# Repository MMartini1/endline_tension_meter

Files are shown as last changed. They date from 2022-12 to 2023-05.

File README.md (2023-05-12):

# endline_tension_meter
 Submersible load cell based endline tension meter

Original design by William DeVoe, Marine Resource Scientist at Maine Department of Marine Resources 

This version is built for the NOAA Northeast Fisheries Science Center and is a work in progress.  The main differences are:
- 3D printed framework to secure the electronics
- detachable wires from the end cap switch
- Qwiic shield to connect from the feather to the sensor board
- different load cell wiring
- larger battery and housing for 6 day endurance 
- add pressure relief valve
- refinements to the code

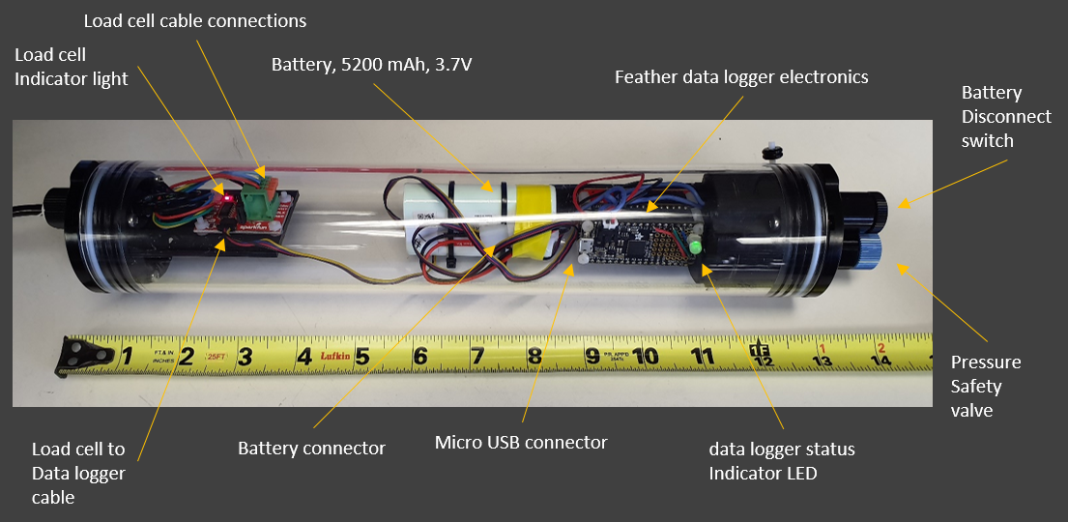
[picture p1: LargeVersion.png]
Image of the load cell logger


This repository is a scientific product and is not official communication of the National Oceanic and Atmospheric Administration, or the United States Department of Commerce. All NOAA GitHub project code is provided on an ‘as is’ basis and the user assumes responsibility for its use. Any claims against the Department of Commerce or Department of Commerce bureaus stemming from the use of this GitHub project will be governed by all applicable Federal law. Any reference to specific commercial products, processes, or services by service mark, trademark, manufacturer, or otherwise, does not constitute or imply their endorsement, recommendation or favoring by the Department of Commerce. The Department of Commerce seal and logo, or the seal and logo of a DOC bureau, shall not be used in any manner to imply endorsement of any commercial product or activity by DOC or the United States Government.

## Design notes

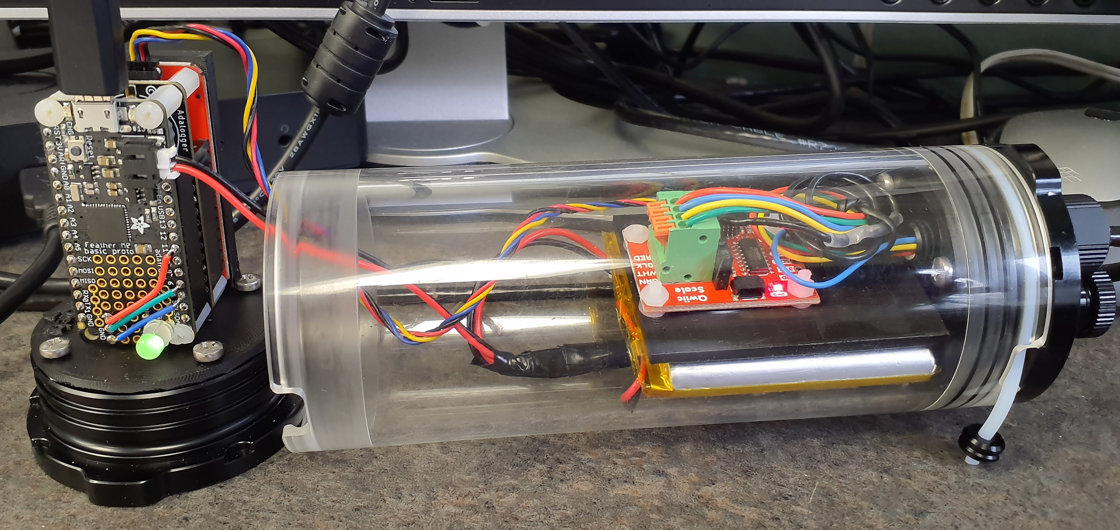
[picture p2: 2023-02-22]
Images/20230206_125726web.jpg

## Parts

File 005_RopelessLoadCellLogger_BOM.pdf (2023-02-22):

Endline Tensiometer Bill of Materials | TOTAL | $ 3,281.87
Purpose/Assembly | Vendor | Item description or part number | Qty | unit cost | total cost | stock #
Load Cell | Load Cell Central Load Cell Central UMLS-51-4.75t on shackle | 1 $ 2,795.00 $ 2,795.00
Load Cell - spare | McMaster | 316 Stainless Steel Cotter Pin
| | 1/8" Diameter, 2" Long, pack of 25 | 1 | | 18.18 $ | 18.18 98355A170
Logger | Adafruit | Adafruit Feather M0 Basic Proto | 1 | 19.95 $ | $ | 19.95 | 2772
Logger alternative | Adafruit | Adafruit Feather M0 Express - ATSAMD21 Cortex M0,
Product ID: 3403 | $ | 19.95 $ | - | 3403

possible logger alternative Adafruit

| | Adafruit Feather M4 Express - Featuring ATSAMD51 -
ATSAMD51 Cortex M4, Product ID: 3857 | $ | 22.95 $ | - | 3857
Logger | Adafruit | Adalogger FeatherWing: SD + RTC | 1 $ | | 8.95 $ | 8.95 | 2922
Logger | Digikey | NAU7802 Weight Scale Sensor Qwiic Platform
Evaluation Expansion Board, Sparkfun SEN-15242, | 1 | 16.50 $ | $ | 16.50 1568-SEN-15242-ND
Logger | Adafruit | Stacking Headers for Feather - 12-pin and 16-pin
female headers, Product ID: 2830 | 3 | 1.25 $ | $ | 3.75 | 2830
Logger | Sparkfun | SparkFun Qwiic Shield for Thing Plus | 1 $ | | 2.97 $ | 2.97 DEV-16790
| Sparkfun | Sparkfun Qwiic Cable
Logger | Western Digital Micro SD Card, 32GB | 2 $ | 10.29 $ | 20.58 SDSQXAF-032G-GN6MA
Logger | Digikey | Coin, 12.5mm Lithium Manganese Dioxide 3 V Battery
Non-Rechargeable (Primary), CR1220 | 2 | 1.13 $ | $ | 2.26 P033-ND
Logger | Adafruit | Diffused RGB 5mm LED (25 pack), Product ID: 302
(common anode) | 1 | 12.50 $ | $ | 12.50 | 302
Logger | Adafruit | Through-Hole Resistors - 22K ohm 5% 1/4W - Pack of
25, Product ID: 2785 | 1 | 0.75 $ | $ | 0.75 | 2785
Logger | Adafruit | Lithium Battery, 2500 mAh LiPo, 3.7v, Product ID 328 | 2 | 14.95 $ | $ | 29.90
Logger - Spare | Digikey | Pushbutton Switch SPST-NO Standard Panel Mount,
Rear, Grayhill P/N 30-3UL, GH1358-ND | $ | 6.26 $ | - GH1358-ND
Logger | Digikey | 0.110" (2.79mm), 0.125" (3.18mm) Quick Connect
| | Female 18-22 AWG Crimp Connector Fully Insulated,
TE Faston 2-520084-2, A27797-ND | 2 | 0.45 $ | $ | 0.90 A27797-ND
005_LoadCellLogger_BOM.xlsx | Page 1

Logger - development | Digikey | Qwiic Cable - Breadboard Jumper (4-pin), Sparkfun
PRT-14425, | 1 | 1.50 $ | $ | 1.50 1568-1709-ND
Logger | Digikey | Flexible Qwiic Cable - 200mm, Sparkfun PRT-17258
ROHS | 1 | 1.60 $ | $ | 1.60 1568-PRT-17258-ND
Logger | Adafruit | FeatherWing Proto - Prototyping Add-on For All
Feather Boards | 1 | 4.95 $ | $ | 4.95 2884
Logger | Digikey | Hex Standoff Threaded M2.5x0.45 Nylon 0.394"
(10.00mm), M2105-2545-N, 1772-2274-ND | 4 | 3.15 $ | $ | 12.60 1772-2274-ND
Logger | Digikey | Hex Standoff Threaded M2.5x0.45 Nylon 0.394"
(10.00mm), RAF M1257-2545-N, 1772-2050-ND | 4 | 1.73 $ | $ | 6.92 1772-2050-ND
Logger | Digikey | M2.5x0.45 Pan Head Machine Screw Phillips Drive
| | Nylon, Essentra 50M025045P012, 145-
50M025045P012-ND | 8 | 0.15 $ | $ | 1.20 145-50M025045P012-ND
Logger | Digikey | M2.5x0.45 Hex Nut 0.190" (4.83mm) Nylon, Essentra
04M025045HN, RPC7085-ND | 8 | 0.12 $ | $ | 0.96 RPC7085-ND
Logger | Digikey | USB 2.0 Cable A Male to Micro B Male 3.28' (1.00m)
Shielded, CNC 102-1492-BL-F0100, 1175-1809-ND | 2 | 6.16 $ | $ | 12.32 1175-1809-ND
Logger | Adafruit | battery charger | 1 $ | 6.95 $ | 6.95 | 1904
Logger | Adafruit | JST PH 2-Pin Cable - Female Connector 100mm
Product ID: 261 | 1 | 0.75 $ | $ | 0.75 | 261
Logger | Adafruit | JST PH 2-Pin Cable – Male Header 200mm
Product ID: 3814 | 1 | 0.75 $ | $ | 0.75 | 3814
Logger | Adafruit | JST-PH Battery Extension Cable - 500mm
| | Product ID: 1131 | 1 | 1.95 $ | 1.95 | 1131
Logger | Adafruit | JST 2-pin Extension Cable with On/Off Switch - JST PH2
| | Product ID: 3064 | 1 | 2.95 $ | 2.95 | 3064
Enclosure | Blue Robotics | Blue Robotics 2"x6" acrylic enclosure | | $ | - next 4 lines
Enclosure | Blue Robotics | Acrylic tube, 150 mm x 50 mm ID, Blue Robotics WTE2-
M-LOCKING-TUBE-150 | 1 | 52.00 $ | $ | 52.00
| | | | | | WTE2-M-LOCKING-TUBE-
150
Enclosure | Blue Robotics | End cap, Al, 50 mm, Blue Robotics WTE2-M-LOCKING-
FLANGE-CAP-BLANK, 950 m | 1 | 30.00 $ | $ | 30.00
| | | | | | WTE2-M-LOCKING-FLANGE-
CAP-BLANK
Enclosure | Blue Robotics | End cap, Al, 50 mm, 2x M10 holes, Blue Robotics,
WTE2-M-LOCKING-FLANGE-CAP-2-HOLE, 950 m | 1 | 32.00 $ | $ | 32.00
| | | | | | WTE2-M-LOCKING-FLANGE-
CAP-2-HOLE
Enclosure | Blue Robotics | Pressure releif valve | 1 $ | 28.00 $ | 28.00 PRV-M10-ASM-R1-RP
Enclosure | Blue Robotics | Blue Robotics On/Off switch | 1 $ | 20.00 $ | 20.00 SWITCH-M10-5A-R1-RP
Enclosure | Blue Robotics | Blue Robotics M10 8mm Cable Penetrator | 2 $ | 6.00 $ | 12.00
005_LoadCellLogger_BOM.xlsx | Page 2

Enclosure | 3D print | Logger internal mount, load cell end | | | $ | -
Enclosure | 3D print | Logger internal mount, blank end | | | $ | -
Enclosure | McMaster | 316 Stainless Steel Pan Head Phillips Screws
M3 x 0.50 mm Thread, 8mm Long, pack of 100 | 1 | 13.24 $ | $ | 13.24 90116A153
Enclosure | Blue Robotics | Bulkhead wrench | 1 | 16.00 $ | $ | 16.00
| | | | | | WL-M10-BULKHEAD-
| | | | | | WRENCH-R1-RP
Sealing | Blue Robotics | Locktite Marine Epoxy | 1 $ | | 10.00 $ | 10.00 LOCTITE-MARINE-EPOXY
Sealing | Blue Robotics | Potting kit (10 pack) | 1 $ | | 10.00 $ | 10.00 TOOL-POTTING-KIT-R1-RP
| | | | | $ | -
Sealing - consider | Blue Robotics | Mityvac Hand Operated Vacuum Pump | $ | 98.00 $ | - VACUUM-PUMP-KIT-R4-RP
Sealing | Blue Robotics | Molykote 111 | 1 | 32.00 $ | $ | 32.00 MOLYKOTE-VP
Sealing | Blue Robotics | Acetone Cable Preparation Wipes (10 pcs) | 1 $ | | 4.00 $ | 4.00 POTTING-ACETONE-WIPES-QTY10-R1-RP
Sealing | Blue Robotics | Vacuum Plug | 1 $ | | 8.00 $ | 8.00 VENT-M10-VACUUM-PLUG-R1-RP
Sealing - consider | Blue Robotics | Cable Repair Kit | $ | 20.00 $ | - TOOL-KIT-CABLE-REPAIR-R1-RP
Sealing - spares | Blue Robotics | Spare Locking Cord and Handles, set of 4 | 1 $ | | 10.00 $ | 10.00 WTE-LOCKING-CORD-SPARE-SET-R1-RP
Sealing - spares | McMaster | Oil-Resistant Buna-N O-Ring, 1/16 Fractional Width,
| | Dash Number 013, pack of 100 | 1 $ | | 5.14 $ | 5.14 9452K57
Sealing - spares | McMaster | Oil-Resistant Buna-N O-Ring, 1/16 Fractional Width,
| | Dash Number 030, pack of 100 | 1 $ | | 11.67 $ | 11.67 9452K117
Sealing | McMaster | Hex L-Key with Standard Tip, 1.5 mm Size, 1-13/16"
| | Overall Length | 1 $ | | 0.23 $ | 0.23 7289A11
005_LoadCellLogger_BOM.xlsx | Page 3

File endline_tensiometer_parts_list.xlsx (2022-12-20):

Endline Tensiometer Parts List
Bill DeVoe, Maine Department of Marine Resources
Group | Part | Price | Link | Comments
Load Cell | Load Cell Central UMLS-51-4.75t | 2795
Logger | Adafruit Feather M0 Basic Proto | 19.95 | https://www.adafruit.com/product/2772 | Should be able to use any Feather compatible microcontroller with minimal changes (if any) to firmware
Logger | Adalogger FeatherWing: SD + RTC | 8.95 | https://www.adafruit.com/product/2922 | Could also use Feather Adalogger M0 for microcontroller with RTC FeatherWing
Logger | SparkFun Qwiic Scale - NAU7802 | 16.5 | https://www.sparkfun.com/products/15242 | Can also use new Adafruit NAU7802 - https://www.adafruit.com/product/4538 - does not have quick connects and library might not be supported?
Logger | Stacking headers
Logger | Piece of stripboard for base
Logger | Micro SD Card
Logger | RGB LED and 22k resistors |  |  | Optional for the load indication LED
Logger | Lithium Battery | 20 | https://www.adafruit.com/product/328 | Can be sized for however long deployment needs to be
Enclosure | Blue Robotics 2"x6" acrylic enclosure | 100 | https://bluerobotics.com/store/watertight-enclosures/wte-vp | End 1 should be aluminum flange solid. End 2 aluminum flange 2 holes
Enclosure | Blue Robotics On/Off switch | 20 | https://bluerobotics.com/store/comm-control-power/switch/switch-10-5a-r1/
Enclosure | Blue Robotics M10 8mm Cable Penetrator | 6 | https://bluerobotics.com/store/cables-connectors/penetrators/penetrator-vp/ | Dependent on the size of the load cell cable
Sealing | Marine Epoxy | 10 | https://bluerobotics.com/store/cables-connectors/tools/loctite-marine-epoxy/ | For potting the cable through the penetrator
Sealing | Potting kits | 10 | https://bluerobotics.com/store/cables-connectors/tools/tool-potting-kit-r1/
Sealing | Silicone grease for end cap seals
Sealing | Optional - Vacuum pump | 100 | https://bluerobotics.com/store/watertight-enclosures/enclosure-tools-supplies/vacuum-pump-kit-r2-rp/ | allows testing enclosure for leaks prior to deployment
Other | solder

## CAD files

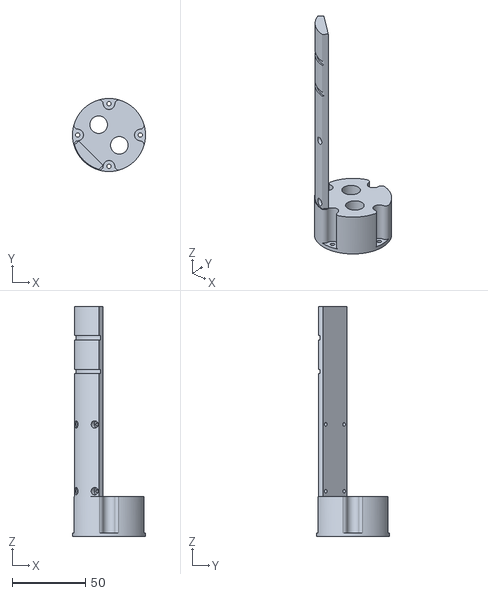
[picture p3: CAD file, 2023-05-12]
3D models/005RLCL-110HousingInternalMountLargeBatt.V2.stl
50.0 x 50.0 x 157.5

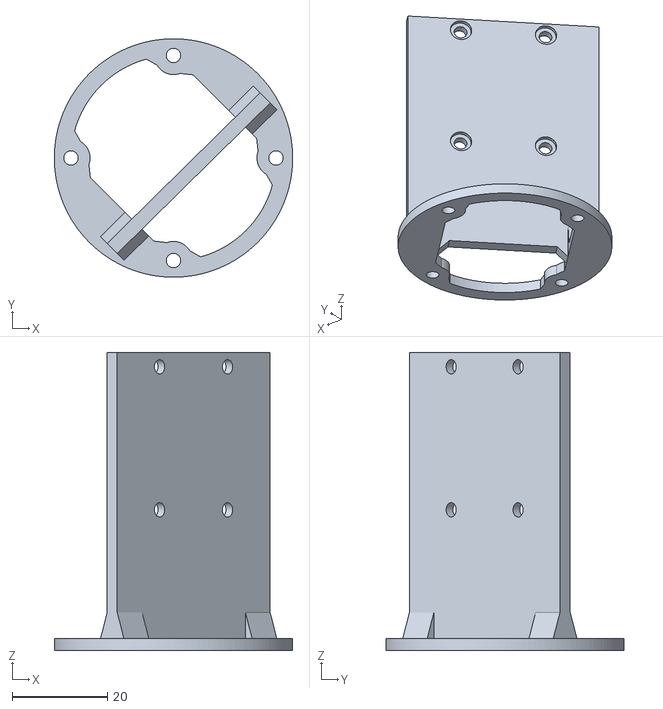
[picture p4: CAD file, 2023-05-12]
3D models/005RLCL-105HousingInternalMountLCend.V2.stl
50.0 x 50.0 x 62.5

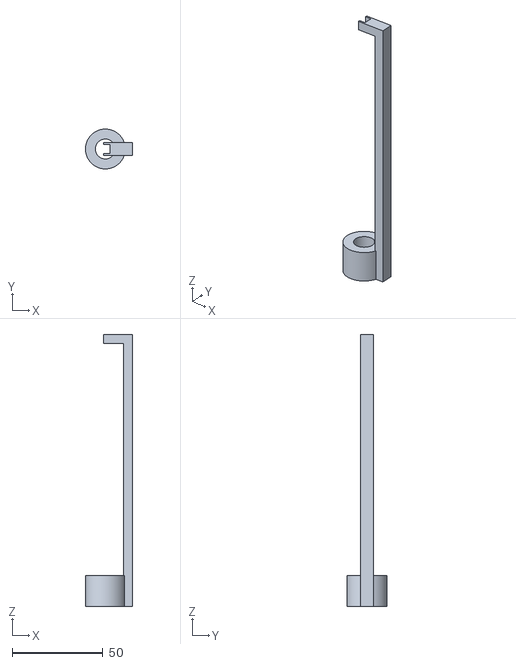
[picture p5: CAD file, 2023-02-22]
3D models/005RLCL-102PottingJig.stl
26.0 x 22.0 x 150.0

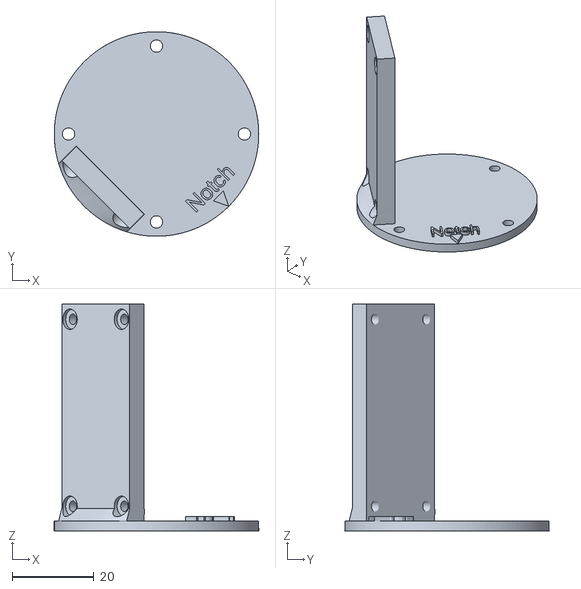
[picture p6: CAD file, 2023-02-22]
3D models/005RLCL-101HousingInternalMount.V4.stl
50.0 x 50.0 x 55.5

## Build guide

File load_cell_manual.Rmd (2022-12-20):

---
title: "Submersible Load Cell Data Logger Manual"
author: "Bill DeVoe"
date: "11/20/2020"
output: html_document
---

```{r setup, include=FALSE}
knitr::opts_chunk$set(echo = TRUE)
```

# Introduction

The submersible load cell data logger excepts load input from a standard four-wire load cell and writes the load value to a CSV file at a predetermined interval.

# Setup

## Load Cell Connection

The load cell should be connected to the green jumper block on the SparkFun Load Cell Amplifier. The jumper block is labeled with standard load cell wire colors; however, the submersible load cell uses non-standard colors. The appropriate connections for the submersible load cell cable are as follows:

```{r echo=FALSE, message=FALSE, warning=FALSE}
lc_conn <- data.frame(load_cell_cable = c('Black', 'White', 'Red', 'Green'),
           logger_terminal = c('Red', 'Black', 'Green', 'White'),
           cable_pin = c(1, 2, 3, 4),
           Function = c('Voltage +', 'Voltage -', 'Signal +', 'Signal -'))
names(lc_conn) <- stringr::str_to_title(gsub('_', ' ', names(lc_conn)))

knitr::kable(lc_conn, align = 'c')

```

## Power

The logger can be powered by a lithium-ion battery plugged into the battery connection on the top circuit board of the logger (the Feather M0 board). The battery can be recharged by connecting a mini-USB cable to the USB connector on the end of the board. Additionally, the logger can be powered by any USB power source connected to this jack, such as a USB power bank. When charging, a red LED on the Feather next to the USB jack will light. It will turn off when the battery is fully charged.

The switch on the outside of the enclosure can be used to turn the logger on and off. It is necessary for the switch to be turned on when charging, such that the battery is connected the board. 

## Memory card

A SD card formatted to FAT32 should be inserted into the memory card slot on the middle circuit board of the logger. Formatting the card with the [official SD association formatter](https://www.sdcard.org/downloads/formatter/) is recommended.

## Stored Settings

Logger settings, including load cell calibration, are stored in a text file `config.txt` on the root level of the SD card. This allows settings to be easily transferred between loggers. If this file is absent, the logger will write this file with the default settings, as specified in the header of the logger source code. The `config.txt` file contains the following settings, one per line:

* `echo = 1` - 1 or 0, whether load cell readings should be echoed over the data logger serial port.
* `log_interval = 250` - The interval in milliseconds between each load cell reading saved to the SD card.
* `sync_interval = 10000` - The interval in milliseconds between data writes to the SD card. Longer intervals save on power consumption, but if power is cut to the logger all data since the last write will be lost. This value must be larger than the `log_interval`.
* `cal_factor = 1` - The calibration factor for the load cell. This can be set using a known weight using the built-in calibration procedure.
* `zero_factor = 0` - The zero factor for the load cell. This can also be set using the built-in calibration procedure.
* `trip_value = 1700` - This value, in calibrated load units, controls the behavior of the RGB LED on the logger board. The RGB LED will indicate when the load cell has reached 50%, 75% and 100% of this value since power up.

## Logger Enclosure

The electronics for the enclosure are enclosed in a Blue Robotics Water Tight Enclosure. This enclosure is submersible up to 100m depth. Blue Robotics has a great guide [here](https://bluerobotics.com/learn/watertight-enclosure-wte-assembly-new/) on assembling and opening these enclosures. Other notes:

* There is silicone grease in the lobster lab for lubricating the gaskets.
* It is recommended to remove only the endcap with the switch and cable penetrators, and leave the solid endcap in place.
* Use of desiccant packs as a fail-safe is helpful.
* The enclosure can be pressure-tested by connecting the included vacuum pump to the switch penetrator (remove the knob), negatively pressuring the enclosure, and monitoring the pressure. Blue Robotics has a guide on this [here](https://bluerobotics.com/learn/using-the-vacuum-test-plug/). While the pump will not apply enough negative pressure to simulate the maximum depth of 100m, it is helpful for checking for leaks.

# RGB LED

A single RGB LED is mounted on the logger base circuit board and is used to convey logger status when the logger is not connected via USB. The RGB LED uses the following color codes:

* `Green` - The logger has successfully powered up, communicated with the load cell, and is writing to the CSV log file.
* `Blue` - The logger battery voltage is less than 3.5 volts, indicating ~20% of the battery life remains. Battery voltage is checked each time the SD card is synced (the `sync_interval` setting.)
* `Magenta` - A critical error has occurred and the logger is unable to record data. For more details, connect to the logger over USB to see debugging output.
* `Pale Yellow` - The maximum load on the load cell since power up has been between 50% and 75% of the `trip_value`.
* `Orange` - The maximum load on the load cell since power up has been between 75% and 100% of the `trip_value`.
* `Red` - The maximum load on the load cell since power up has exceeded the `trip_value`.

# CSV Format

A new CSV file is created each time the logger powers on. CSV filenames are eight characters in length and contain the date followed by a sequential identifier 01-99. The format is therefore `{two-digit year}{zero-padded month}{zero-padded day}{01-99}.csv`. If the logger is powered on more than 99 times in a day, this will likely produce an error. This is a result of SD library used in the logger firmware, which uses DOS 8.3 filenames (eight characters in length maximum). 

The produced CSVs contain the following fields:

* `millis` - The number of milliseconds since the logger powered on.
* `time` - The load cell reading timestamp in ISO format, yyyy-MM-ddThh:mm:ss.sZ, where the Z indicates the timezone as UTC.
* `raw_load` - The raw load output by the SparkFun Load Cell Amplifier. This is NOT the load cell output in mV/V, but rather a unitless value specific to the chipset used.
* `load` - The calibrated load value - this is a result of solving the line equation using raw load and stored settings, `load = cal_factor * raw_load + zero_offset`.

# Serial Interface

Commands can be sent to the logger over the USB interface, using a serial terminal program like PuTTY or the Arduino Serial Monitor. This can be used to debug the logger and change settings (which can also be changed by editing the CONFIG.TXT file.)

To connect to the logger, use a serial baud rate of 9600.

The following serial output indicates successful load cell power up:

```{}
----------------------------------------
      Lobster Endline Tension Meter

Created by Bill DeVoe, MaineDMR
For questions, email william.devoe@maine.gov
----------------------------------------
Init SD card
SD card OK

RTC OK

LC OK

LC 0 offset: 1000
LC cali factor: 0.00

Logging to: 20102202.CSV at 1000ms interval.

Type the following menu commands at any time:
 l - Change logging interval
 s - Change card sync interval
 e - Toggle echo to serial
 z - Get current real-time clock time
 d - Set real-time clock time
 c - Calibrate load cell with known weight
 m - Manually calibrate load cell with known values
 v - Retrieve load cell calibration values 
 t - Tare the load cell
 f - Enter the file manager.
Type menu CMD any time.

RGB set to:
0
255
0
```

Once the logger is recording, if `echo to serial` is enabled, each load cell reading will be output to the terminal. This out is identical to the data written to the CSV file:

```{}
46292,2020-10-22T12:42:22Z,2101,0.01
47292,2020-10-22T12:42:23Z,2194,0.1
48292,2020-10-22T12:42:24Z,2565,0.5
```

If the last value (the calibrated load) is `inf` or `NaN`, this indicates the cell has not been calibrated.

Menu options are available for multiple functions. In general, guidance on how to use these functions will be printed to the console as they are accessed.

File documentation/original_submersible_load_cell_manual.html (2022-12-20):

# Submersible Load Cell Data Logger Manual

#### Bill DeVoe

#### 11/20/2020

# Introduction

The submersible load cell data logger excepts load input from a standard four-wire load cell and writes the load value to a CSV file at a predetermined interval.

# Setup

## Load Cell Connection

The load cell should be connected to the green jumper block on the SparkFun Load Cell Amplifier. The jumper block is labeled with standard load cell wire colors; however, the submersible load cell uses non-standard colors. The appropriate connections for the submersible load cell cable are as follows:

Load Cell Cable | Logger Terminal | Cable Pin | Function
Black | Red | 1 | Voltage +
White | Black | 2 | Voltage -
Red | Green | 3 | Signal +
Green | White | 4 | Signal -

## Power

The logger can be powered by a lithium-ion battery plugged into the battery connection on the top circuit board of the logger (the Feather M0 board). The battery can be recharged by connecting a mini-USB cable to the USB connector on the end of the board. Additionally, the logger can be powered by any USB power source connected to this jack, such as a USB power bank. When charging, a red LED on the Feather next to the USB jack will light. It will turn off when the battery is fully charged.

The switch on the outside of the enclosure can be used to turn the logger on and off. It is necessary for the switch to be turned on when charging, such that the battery is connected the board.

## Memory card

A SD card formatted to FAT32 should be inserted into the memory card slot on the middle circuit board of the logger. Formatting the card with the official SD association formatter (https://www.sdcard.org/downloads/formatter/) is recommended.

## Stored Settings

Logger settings, including load cell calibration, are stored in a text file config.txt on the root level of the SD card. This allows settings to be easily transferred between loggers. If this file is absent, the logger will write this file with the default settings, as specified in the header of the logger source code. The config.txt file contains the following settings, one per line:

- echo = 1 - 1 or 0, whether load cell readings should be echoed over the data logger serial port.
- log_interval = 250 - The interval in milliseconds between each load cell reading saved to the SD card.
- sync_interval = 10000 - The interval in milliseconds between data writes to the SD card. Longer intervals save on power consumption, but if power is cut to the logger all data since the last write will be lost. This value must be larger than the log_interval.
- cal_factor = 1 - The calibration factor for the load cell. This can be set using a known weight using the built-in calibration procedure.
- zero_factor = 0 - The zero factor for the load cell. This can also be set using the built-in calibration procedure.
- trip_value = 1700 - This value, in calibrated load units, controls the behavior of the RGB LED on the logger board. The RGB LED will indicate when the load cell has reached 50%, 75% and 100% of this value since power up.

## Logger Enclosure

The electronics for the enclosure are enclosed in a Blue Robotics Water Tight Enclosure. This enclosure is submersible up to 100m depth. Blue Robotics has a great guide here (https://bluerobotics.com/learn/watertight-enclosure-wte-assembly-new/) on assembling and opening these enclosures. Other notes:

- There is silicone grease in the lobster lab for lubricating the gaskets.
- It is recommended to remove only the endcap with the switch and cable penetrators, and leave the solid endcap in place.
- Use of desiccant packs as a fail-safe is helpful.
- The enclosure can be pressure-tested by connecting the included vacuum pump to the switch penetrator (remove the knob), negatively pressuring the enclosure, and monitoring the pressure. Blue Robotics has a guide on this here (https://bluerobotics.com/learn/using-the-vacuum-test-plug/). While the pump will not apply enough negative pressure to simulate the maximum depth of 100m, it is helpful for checking for leaks.

# RGB LED

A single RGB LED is mounted on the logger base circuit board and is used to convey logger status when the logger is not connected via USB. The RGB LED uses the following color codes:

- Green - The logger has successfully powered up, communicated with the load cell, and is writing to the CSV log file.
- Blue - The logger battery voltage is less than 3.5 volts, indicating ~20% of the battery life remains. Battery voltage is checked each time the SD card is synced (the sync_interval setting.)
- Magenta - A critical error has occurred and the logger is unable to record data. For more details, connect to the logger over USB to see debugging output.
- Pale Yellow - The maximum load on the load cell since power up has been between 50% and 75% of the trip_value.
- Orange - The maximum load on the load cell since power up has been between 75% and 100% of the trip_value.
- Red - The maximum load on the load cell since power up has exceeded the trip_value.

# CSV Format

A new CSV file is created each time the logger powers on. CSV filenames are eight characters in length and contain the date followed by a sequential identifier 01-99. The format is therefore {two-digit year}{zero-padded month}{zero-padded day}{01-99}.csv. If the logger is powered on more than 99 times in a day, this will likely produce an error. This is a result of SD library used in the logger firmware, which uses DOS 8.3 filenames (eight characters in length maximum).

The produced CSVs contain the following fields:

- millis - The number of milliseconds since the logger powered on.
- time - The load cell reading timestamp in ISO format, yyyy-MM-ddThh:mm:ss.sZ, where the Z indicates the timezone as UTC.
- raw_load - The raw load output by the SparkFun Load Cell Amplifier. This is NOT the load cell output in mV/V, but rather a unitless value specific to the chipset used.
- load - The calibrated load value - this is a result of solving the line equation using raw load and stored settings, load = cal_factor * raw_load + zero_offset.

# Serial Interface

Commands can be sent to the logger over the USB interface, using a serial terminal program like PuTTY or the Arduino Serial Monitor. This can be used to debug the logger and change settings (which can also be changed by editing the CONFIG.TXT file.)

To connect to the logger, use a serial baud rate of 9600.

The following serial output indicates successful load cell power up:

----------------------------------------
      Lobster Endline Tension Meter

Created by Bill DeVoe, MaineDMR
For questions, email william.devoe@maine.gov
----------------------------------------
Init SD card
SD card OK

RTC OK

LC OK

LC 0 offset: 1000
LC cali factor: 0.00

Logging to: 20102202.CSV at 1000ms interval.

Type the following menu commands at any time:
 l - Change logging interval
 s - Change card sync interval
 e - Toggle echo to serial
 z - Get current real-time clock time
 d - Set real-time clock time
 c - Calibrate load cell with known weight
 m - Manually calibrate load cell with known values
 v - Retrieve load cell calibration values 
 t - Tare the load cell
 f - Enter the file manager.
Type menu CMD any time.

RGB set to:
0
255
0

Once the logger is recording, if echo to serial is enabled, each load cell reading will be output to the terminal. This out is identical to the data written to the CSV file:

46292,2020-10-22T12:42:22Z,2101,0.01
47292,2020-10-22T12:42:23Z,2194,0.1
48292,2020-10-22T12:42:24Z,2565,0.5

If the last value (the calibrated load) is inf or NaN, this indicates the cell has not been calibrated.

Menu options are available for multiple functions. In general, guidance on how to use these functions will be printed to the console as they are accessed.

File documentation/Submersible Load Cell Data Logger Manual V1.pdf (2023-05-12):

5/12/2023 10:54 AM | Submersible Load Cell Data Logger Manual (NOAA NEFSC version)

# Submersible Load Cell Data Logger Manual

### Bill DeVoe 11/20/2020 Updates by Marinna Martini April, 2023

# Introduction

This instrument takes the output from a four-wire load cell and both logs it to a microSD card and if requested, displays the data to a serial port (USB). It must be calibrated before use.
The electronics are off the shelf: a Sparkfun scale interface and an Adafruit Feather system with an oversized Lithium-ion battery in a Blue Robotics acrylic housing.
The system was first conceived by William DeVoe of the Maine Department of Marine Resources and has been upgraded and repackaged for longer deployment duration by Marinna Martini of the NOAA Northeast Fisheries Science Center.

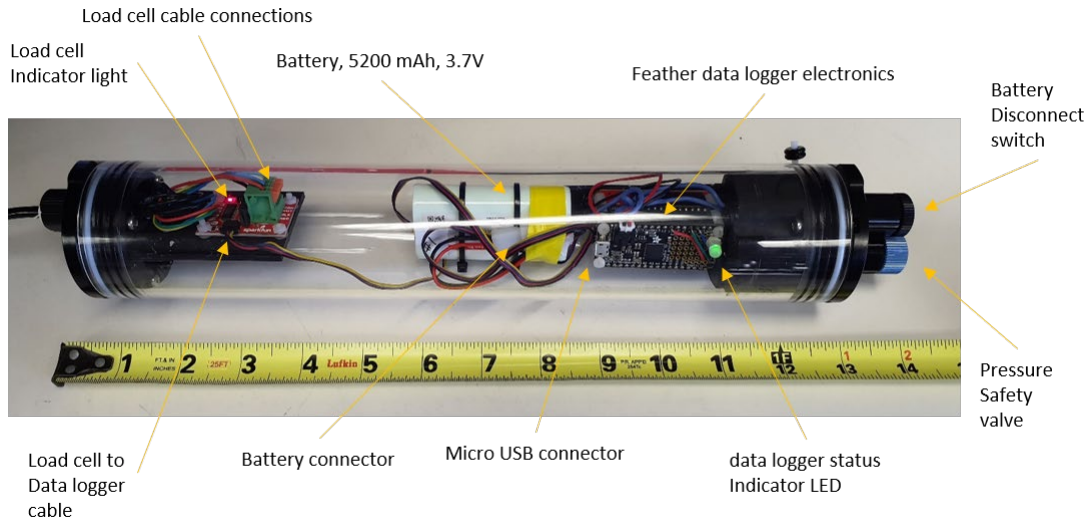
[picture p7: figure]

Figure 1: Parts of the load cell logger.

# Setup

# Load Cell Connection

The load cell should be connected to the green jumper block on the SparkFun Load Cell Amplifier. The jumper block is labeled with standard load cell wire colors; however, the NEFSC submersible load cell uses non-standard colors. The appropriate connections for the NEFSC submersible load cell cable are as follows:
Load Cell Cable | Logger Terminal | Spring Connector Pin | Function
Red | Red | 1 | Voltage +
Blue | Black | 2 | Voltage -
Yellow | White | 3 | Signal +
Green | Green | 4 | Signal -

There is an additional black wire on the NEFSC load cell that is to the shield of the cable and it goes to YLW/SD, the label for which is inconveniently hidden on the bottom of the board. A black header has been added next to the spring connector. The black “shield” wire gets inserted into the 3rd hole on the header. The third hole should be marked, if not, it is the third hole from the end of the connector closest to the label “Qwiic Scale” on the board. See Figure 2.

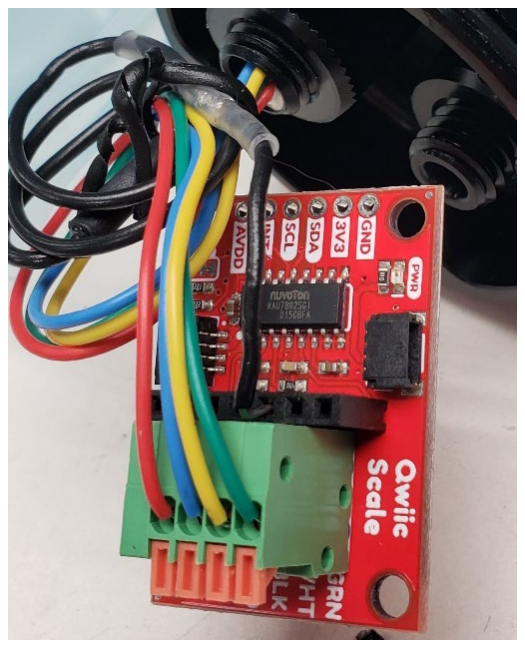
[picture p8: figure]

Figure 2: Hook up for the NEFSC load cell.

# Power

The logger can be powered by a lithium-ion battery plugged into the battery connection on the top circuit board of the logger (the Feather M0 board). The lower capacity battery can be recharged by connecting a mini-USB cable to the USB connector on the end of the board. Additionally, the logger can be powered by any USB power source connected to this jack, such as a USB power bank. If being charged by the Feather, a red LED on the Feather next to the USB jack will light. It will turn off when the battery is fully charged.
Users have a choice of two batteries to operate the logger. Batteries must be 3.7V:
- Lithium ion rechargeable 2500 mAh, Adafruit part #328, is a small, flat cell that will fit in a smaller housing under the and will last about 2 days. It can be recharged by the Feather, while connected to the Feather and the enclosure end cap switch is turned on.
- Lithium ion rechargeable 5200 mAh, Tenergy part #31001, is an oblong battery pack that requires the larger housing (Figure 1) to accommodate, and will last about 6 days. It is best to use the Tenergy smart charger to recharge these batteries while disconnected from the data logger. The charger is Tenergy model TLP-4000; part #01281.

# Memory card

A microSD card formatted to FAT32 should be inserted into the memory card slot on the middle circuit board of the logger. Formatting the card with the official SD association formatter before use (https://www.sdcard.org/downloads/formatter/) is recommended.
The logger is mounted with the memory card abutting the end cap. This is intentional, so that the microSD card is less likely to become unseated. To download files from the card, it is best to use the serial terminal and the file menu. To remove the microSD card, one will need to remove the logger from its mount.

# Stored Settings

Logger settings, including load cell calibration, are stored in a text file config.txt on the root level of the SD card. This allows settings to be easily transferred between loggers. If this file is absent, the logger will write this file with the default settings, as specified in the header of the logger source code. The config.txt file contains the following settings, one per line:
echo = 1 - 1 or 0, whether load cell readings should be echoed over the data logger serial ort. log_interval = 250 - The interval in milliseconds between each load cell reading saved to the SD card. sync_interval = 10000 - The interval in milliseconds between data writes to the SD card. Longer intervals
save on power consumption, but if power is cut to the logger all data since the last write will be lost. This value must be larger than the log_interval .
cal_factor = 1 - The calibration factor for the load cell. This can be set using a known weight using the
built-in calibration procedure.
zero_factor = 0 - The zero factor for the load cell. This can also be set using the built-in calibration
procedure.
trip_value = 1700 - This value, in calibrated load units, controls the behavior of the RGB LED on the logger board. The RGB LED will indicate when the load cell has reached 50%, 75% and 100% of this value since power up.

# Logger Enclosure

The electronics for the enclosure are enclosed in a Blue Robotics Water Tight Enclosure. This enclosure is submersible up to 100m depth. Blue Robotics housing information can be found here: https://bluerobotics.com/store/watertight-enclosures/locking-series/wte-locking-tube-r1-vp/, including assembling and opening these enclosures. (https://bluerobotics.com/learn/watertight-enclosure-wte-assembly-new/)
- O-rings on the end caps should be cleaned and inspected, each time the end cap is opened and preferably replaced, for each deployment. These are Dash #030, McMaster part # 9452K117, or Blue Robotics kit https://bluerobotics.com/store/retired/wte2-o-ring-set-r1/. Note this housing does not have a face seal.
- O-rings on the penetrators for the load cell cable, the pressure relief valve and the switch are Dash #013, McMaster part # 9452K57. Blue Robotics also sells packs of these that are blue colored, which is better as it makes it easier to confirm the o-ring is seated properly. https://bluerobotics.com/store/cables-connectors/penetrators/penetrator-o-ring-set-r1/
- The NEFSC version has added the pressure relief valve for safety. Learn about the valve here: https://bluerobotics.com/learn/pressure-relief-valve-installation-and-usage/.
- On recovery, the safest way to access the housing is to unscrew the relief valve first, and allow pressure to equilibrate. Be sure to check the O-rings and screw it back on before deployment!
- If there is a vacuum in the housing, or less pressure than outside, the end cap will be very hard to remove. This might happen if the housing was sealed on a warm day and recovered on a cooler day, or never warms up for water temperature.
- If there is more pressure in the housing than outside, then when the locking thread is removed, the end cap might come flying off, neither good for the person servicing the housing or the electronics. This might happen if the housing is sealed on a cold day and then warmed up.
- All O-rings should be kept greased with a light coating of silicone grease, Molykote 111 compound. Blue Robotics sells packets of this, and it is McMaster #1204K32.

- It is recommended to remove only the endcap with the switch and cable penetrators, and leave the load cell endcap in place.
- Be mindful off the potted connector to the load cell cable, repotting will be necessary if this is damaged.
- Use of desiccant packs as a fail-safe is helpful.
- The enclosure can be pressure-tested by connecting the included vacuum pump to the switch penetrator (remove the knob), negatively pressuring the enclosure, and monitoring the pressure. Blue Robotics has a guide on this here (https://bluerobotics.com/learn/using-the-vacuum-test-plug/). (https://bluerobotics.com/learn/using-the-vacuum-test-plug/) While the pump will not apply enough negative pressure to simulate the maximum depth of 100m, it is helpful for checking for leaks.
- A hand vacuum pump sold by Blue Robotics is here: https://bluerobotics.com/store/watertight-enclosures/enclosure-tools-supplies/vacuum-pump-kit-r2-rp/ (https://bluerobotics.com/store/watertight-enclosures/enclosure-tools-supplies/vacuum-pump-kit-r2-rp/)

# RGB LED

A single RGB LED is mounted on the logger base circuit board and is used to convey logger status when the logger is not connected via USB. The RGB LED uses the following color codes:
- Green - The logger has successfully powered up, communicated with the load cell, and is writing to the CSV log file.
- Blue – The logger battery voltage is less than 3.5 volts:
- For the small, flat, 2500 mAh battery, this indicates that ~20% of the battery life remains.
- For the large, 5200 mAh battery, this indicates that ~60% of the battery life remains.
- Battery voltage is checked each time the SD card is synced (the sync_interval setting.).
- Magenta - A critical error has occurred and the logger is unable to record data. For more details, connect to the logger over USB to see debugging output.
- Pale Yellow - The maximum load on the load cell since power up has been between 50% and 75% of the trip_value .
- Orange - The maximum load on the load cell since power up has been between 75% and 100% of the trip_value .
- Red - The maximum load on the load cell since power up has exceeded the trip_value .

The LED might turn red if the load cell shackle is dropped or handled. If the RGB turns red while one is preparing for deployment, this can be cleared by turning the power on and off to the logger by using the switch on the end cap. Make sure the LED is green on deployment.

# CSV Format

A new CSV file is created each time the logger powers on. CSV filenames are eight characters in length and contain the date followed by a sequential identifier 01-99. The format is therefore
{two-digit year}{zero-padded month}{zero-padded day}{01-99}.csv . If the logger is powered on more than 99 times in a day, this will likely produce an error. This is a result of SD library used in the logger firmware, which uses DOS 8.3 filenames (eight characters in length maximum).
The produced CSVs contain the following fields:

millis - The number of milliseconds since the logger powered on.
time - The load cell reading timestamp in ISO format, yyyy-MM-ddThh:mm:ss.sZ, where the Z indicates the
timezone as UTC.
raw_load - The raw load output by the SparkFun Load Cell Amplifier. This is NOT the load cell output in
mV/V, but rather a unitless value specific to the chipset used. load - The calibrated load value - this is a result of solving the line equation using raw load and stored
settings, load = cal_factor * raw_load + zero_offset .

# The Serial Interface

One connects to the Feather logger via the USB connector on the Feather card, see Figure 1.

# Selecting a serial interface program

There are two specific operations in using the logger which require certain capabilities in a serial interface. These are the entry of the load when calibrating the load cell and downloading data files over serial. Calibration requires entry of multiple characters on a single line to enter the load on the cell. If you need to download data from the uSD card without removing it, you will need a serial terminal emulation program that will allow logging. For this, the program RealTerm is recommended (https://realterm.sourceforge.io/).
For simple monitoring and one character command operation, PuTTY and Hyperterminal will work. PuTTY is easy to find and download, the old windows hyperterm is no longer supported by windows and download sites might be unreliable. Hilgraeve makes a paid modern version that has not been tested for this use.
Commands can be sent to the logger over the USB interface, using a serial terminal program like PuTTY or the Arduino Serial Monitor. This can be used to debug the logger and change settings (which can also be changed by editing the CONFIG.TXT file.)

# Using a serial interface program

Realterm is used here to show how to communicate with the logger via a serial terminal, enter multiple characters (such as when entering the load during calibration) and download data. To connect to the logger, use a serial baud rate of 9600, No parity, 8 data bits, 1 stop bit and No flow control.

The following serial output indicates successful load cell power up:

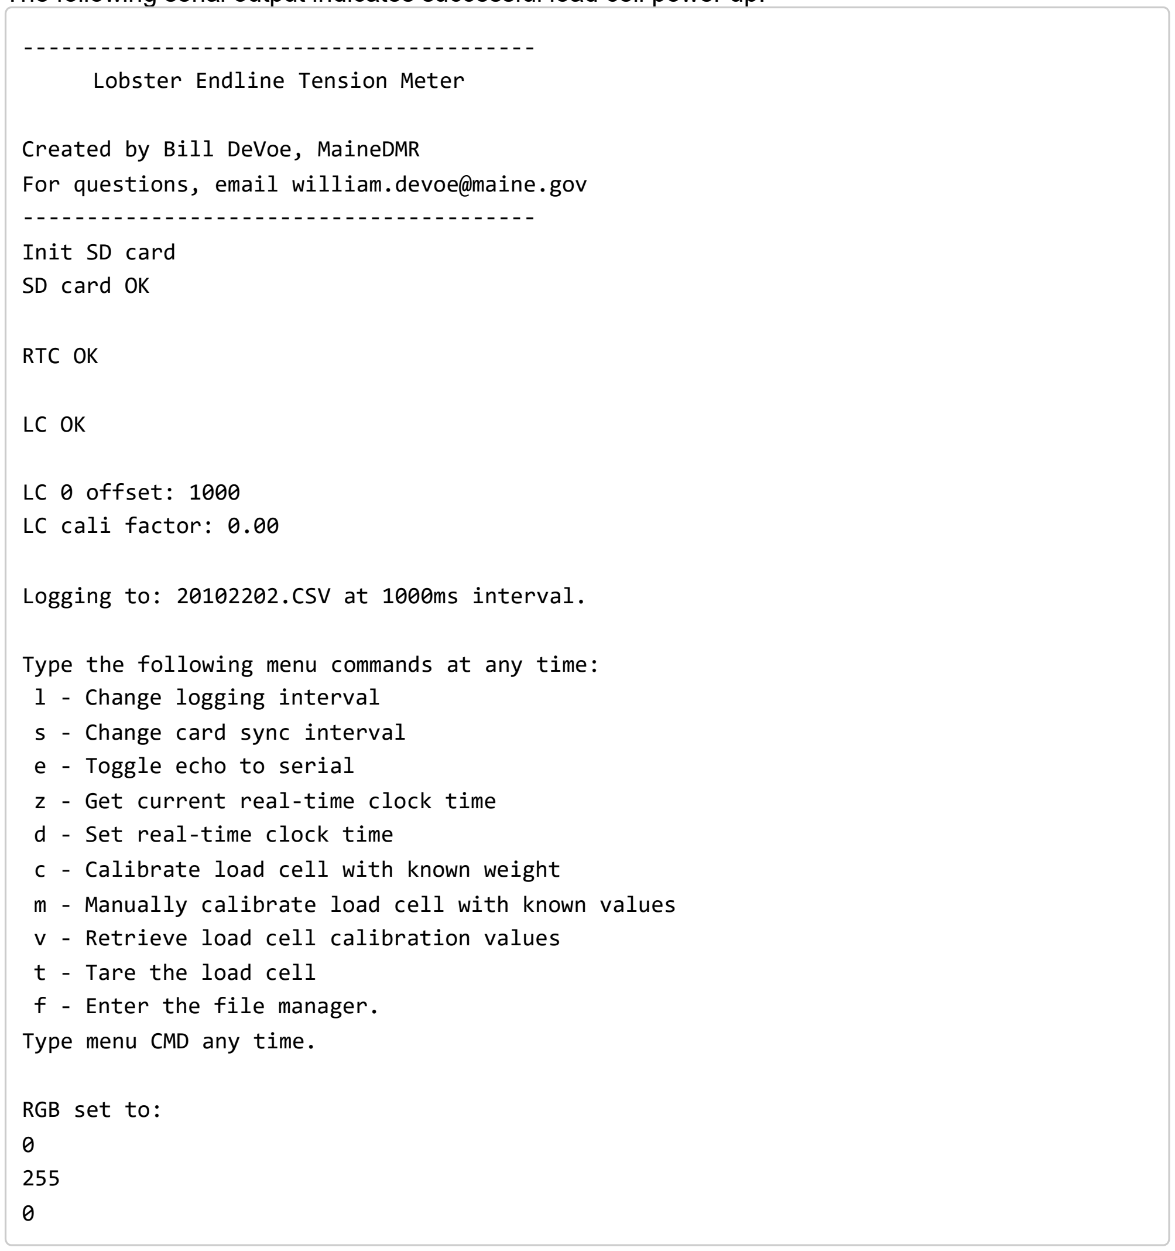
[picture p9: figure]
---------------------------------------- Lobster Endline Tension Meter; Created by Bill DeVoe, MaineDMR For questions, email william.devoe@maine.gov ---------------------------------------- Init SD card SD card OK; RTC OK; LC 0 offset: 1000 LC cali factor: 0.00; l - Change logging interval s - Change card sync interval e - Toggle echo to serial z - Get current real-time clock time d - Set real-time clock time; t - Tare the load cell f - Enter the file manager. Type menu CMD any time.; RGB set to: 0 255 0

Once the logger is recording, if echo to serial is enabled, each load cell reading will be output to the terminal.
This output is identical to the data written to the CSV file:

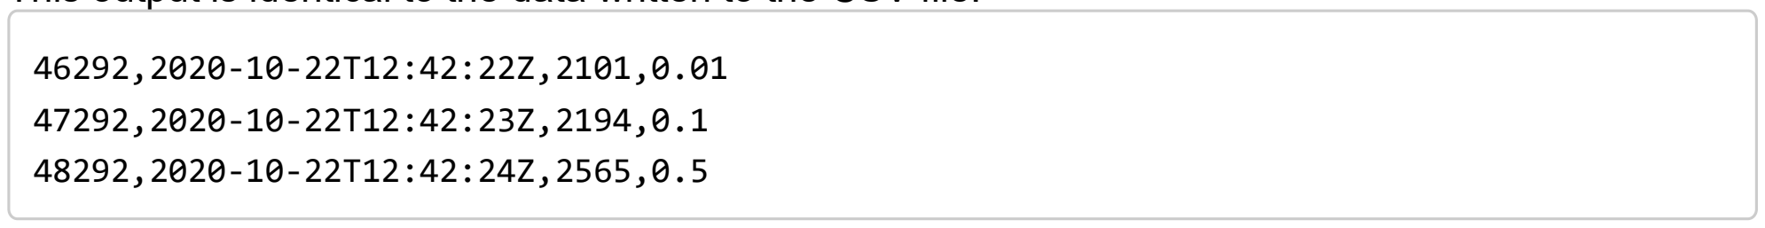
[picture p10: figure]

If the last value (the calibrated load) is inf or NaN, this indicates the cell has not been calibrated.

Logging to: 20102202.CSV at 1000ms interval.

Type the following menu commands at any time:

c - Calibrate load cell with known weight
m - Manually calibrate load cell with known values v - Retrieve load cell calibration values

Menu options are available for multiple functions. In general, guidance on how to use these functions will be printed to the console as they are accessed.
Setting the clock looks like:

Retrieving load cell calibration values looks like:

Calibrating, or manually entering the calibration factors looks like:

--- Set RTC ---

Provide a UTC datetime.
Enter year:
Enter month:
Enter day:
Enter hour (24 format):
Enter minute:
Enter second:
Press any key when ready to set time... 283022,2023-05-11T12:16:30Z,-2107,0.00

484384,2023-05-11T12:19:51Z,-1831,nan

Are you sure you want to change the calibration? Enter y to continue, any other key to abort:

Enter the 0 offset: -1047
Enter the cali factor: 44.50
LC calibrated

LC 0 offset: -1047
LC cali factor: 44.50
LC gain: 16
LC trip value: 1700

507989,2023-05-11T12:20:15Z,-2164,0.00

LC 0 offset: -1047
LC cali factor: 44.00
LC gain: 16
LC trip value: 1700

# Appendices

Troubleshooting • Values of 99999 are reported for computed weight: No readings are being obtained from the

load cell. Power cycle logger.
- Values of 0 are reported for raw weight: No readings are being obtained from the load cell. Power cycle logger.
- The battery level sense will trigger at 3.5V, turning the LED blue. If the Tenergy high capacity battery is in use, this is at about 60% of capacity.

# Realterm

Installing
1. Download Realterm from SourceForge https://sourceforge.net/projects/realterm/
2. Run the installer, admin rights will be needed.
3. Do leave register automation server checked.
4. Realterm will not automatically be added to the start menu. It is installed to the directory C:\Program Files (x86)\BEL\Realterm, so go there and right click on realterm.exe and select “pin to start”. One can always find realterm by typing realterm in the windows search bar.
5. To make start up easier, create a shortcut with the following in the Target box:
"C:\Program Files (x86)\BEL\Realterm\realterm.exe" display=1 scrollback=50 baud=9600 flow=0 capdirect capfile=.\capture.txt
6. Put your shortcut in a convenient place where you will also download your data files.
7. Realterm’s documentation can be found here: https://realterm.sourceforge.io/
Running & connecting
1. Plug in the load cell logger with the USB cable (USB A to USB Micro B).
2. Determine which COM port has been assigned by windows to the logger.
a. Bring up the device manager:
i. Type devmgmt in the search bar or in a cmd window or ii. In windows settings search for device manager
b. When it warns you you are a standard user, say OK
c. In the device manager, find “Ports (COM & LPT)
d. The logger will appear as “USB Serial Device (COMXX). Note the COM number.
e. If you are not sure – unplug and replug the logger, observing which port disappears and reappears in the device manager
3. Run realterm.
4. In the Display tab, it is important that these things are set (should be automatic if your shortcut is set up):
a. Display as: Ansi
b. Rows:10
c. Scroll Back: ticked
5. In the Port tab, it is important that these things are set (should be automatic if your shortcut is set up):
a. Baud: 9600
b. Port to the port you determined earlier (may look like “15 = \USBSER000”)
c. Click on change to apply the new settings

Interacting with the logger
- You can enter single character commands by clicking in the terminal window and typing the character. A good test is the “e” command, which will turn the data echo on or off. Sometimes it will take a few tries to slip a character into the busy logger between readings. Downloading files with realterm
1. It is helpful to have the file folder to which you will capture data files open.
2. In the terminal window, enter f and get to the file menu
3. In the terminal window, enter l to list files, note the name of the file you want to download
4. In the file window, enter t to transfer, you should see “Enter FN:”
5. Go to the Capture tab
a. File: Enter the path and file name, or “…” browse to a directory
b. Click “start overwrite” or “start append”
c. Do not untick direct capture to make sure all data is transmitted
6. Go to the send tab
a. Type in the file name, which is typically YYMMDDXX.CSV
b. Click “send ASCII”
c. Watch the animation in the upper left corner of reaterm’s window, a red square orbiting the terminal icon. This means data is transmitting even if it doesn’t appear on the screen.
7. Wait for the animation or data scrolling to stop.
8. Back at the capture tab, stop capture

9. Check the file folder, did the data arrive intact? Inspect the file, does it start with
10. Does it end with:
11. Does the file name in the header match the file name of your captured file?
12. Are there gaps (empty lines) in the data or truncated lines?
13. There might be some extra text from your session. This can be deleted.
14. For more files, repeat steps 3-10
15. When done, select the file option x to exit the file manager

# Jupyter

Install Anaconda’s miniconda. Either Anaconda or miniconda will install Jupyter.
Jupyter is run by starting an anaconda prompt window and typing “jupyter lab”.
There is a trick to starting Jupyter Lab where you want. If Jupyter Lab is started from a directory on drive C, you can’t get to drive D, where our ITD likes to put all our project files.
- Open cmd (or Anaconda Prompt) and run jupyter notebook --generate-config. This writes a file to C:\Users\username\.jupyter\jupyter_lab_config.py.
- Browse to the file location and open it in an Editor
- Search for the following line in the file:
# c.ServerApp.notebook_dir = ‘'

- Replace with:
c.ServerApp.notebook_dir = 'D:/MyDirectory/Ropeless/LoadCellLogger/Code/'
- Make sure you use forward slashes in your path and use /home/user/ instead of ~/ for your home directory, backslashes could be used if placed in double quotes even if folder name contains spaces as such : "D:\yourUserName\Any Folder\More Folders\"
- Remove the # at the beginning of the line to allow the line to execute

FILE: 23041201.CSV

File dump from 23041201.CSV

millis,time,raw_load,load

Done!

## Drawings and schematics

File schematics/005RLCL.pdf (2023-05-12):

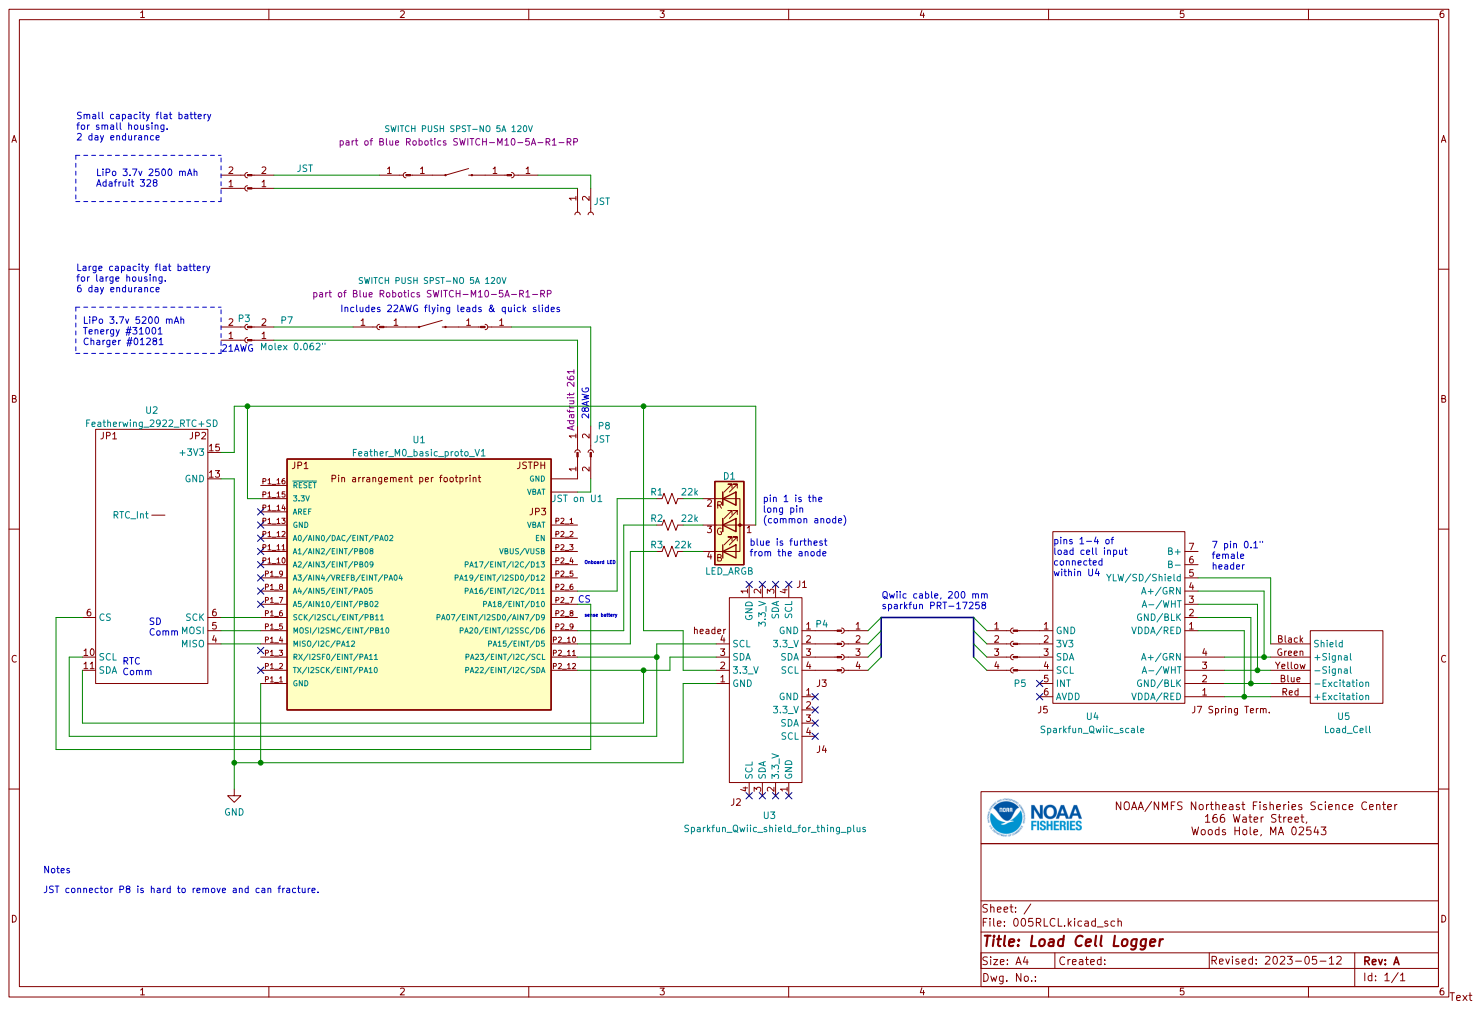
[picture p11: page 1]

SWITCH PUSH SPST-NO 5A 120V

Onboard LED Large capacity flat battery
for large housing.
6 day endurance

1 SWITCH PUSH SPST-NO 5A 120V

part of Blue Robotics SWITCH-M10-5A-R1-RP
Includes 22AWG flying leads & quick slides

header LiPo 3.7v 5200 mAh Tenergy #31001

pins 1-4 of
load cell input connected within U4

3 SDA 3 SDA 3 SCL 4 SCL

JST connector P8 is hard to remove and can fracture. RTC Comm

File: 005RLCL.kicad_sch Sheet: / NOAA/NMFS Northeast Fisheries Science Center

Id: 1/1 Title: Load Cell Logger

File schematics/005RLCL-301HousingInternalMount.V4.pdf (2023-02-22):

53.00

.139

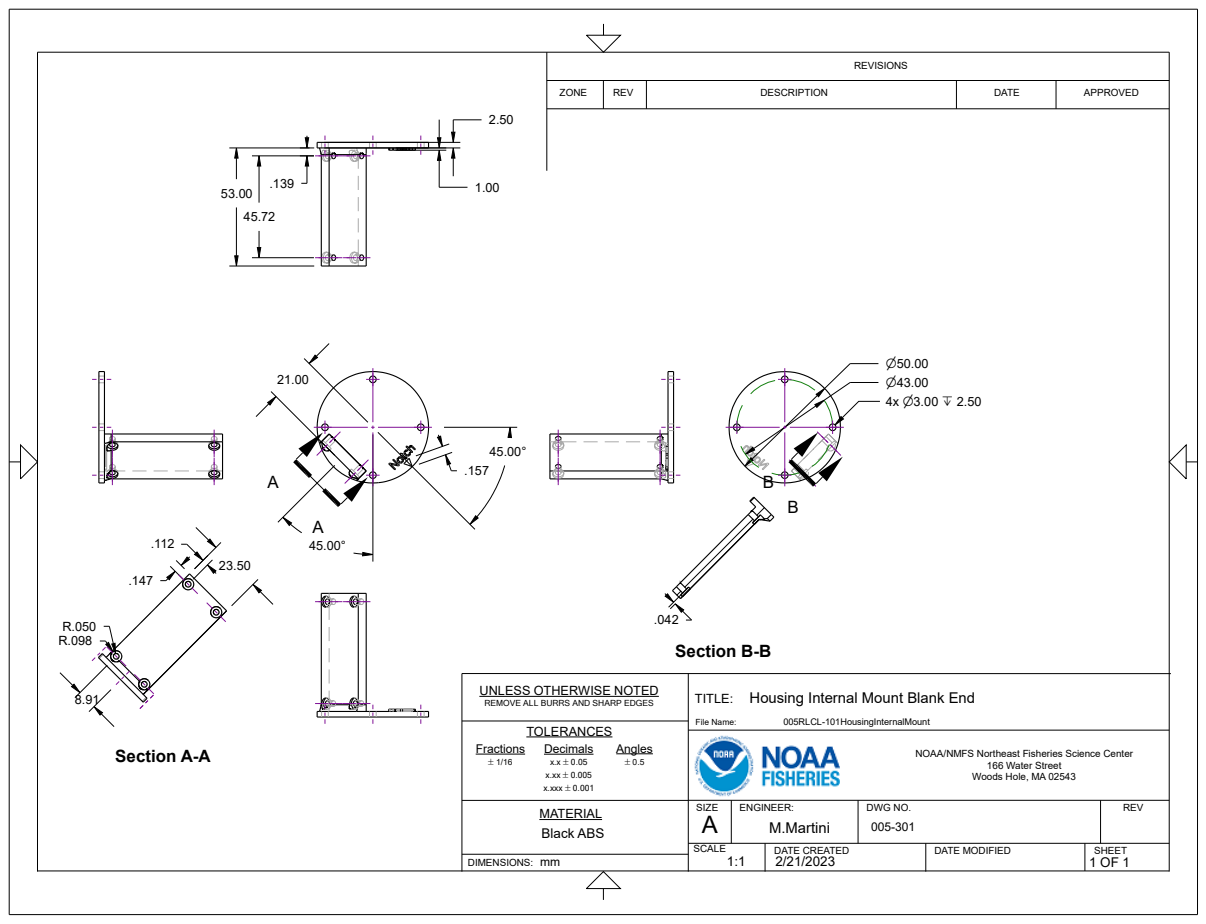
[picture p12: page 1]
Section A-A; Section B-B; DIMENSIONS:; Angles `0.5; TOLERANCES Decimals x.x `0.05 x.xx `0.005 x.xxx `0.001; File Name:; Fractions `1/16; 005RLCL-101HousingInternalMount

REVISIONS

ZONE | REV | DESCRIPTION | DATE | APPROVED

TITLE: UNLESS OTHERWISE NOTED REMOVE ALL BURRS AND SHARP EDGES

Housing Internal Mount Blank End

NOAA/NMFS Northeast Fisheries Science Center

166 Water Street
Woods Hole, MA 02543

Black ABS | SIZE A MATERIAL | ENGINEER: M.Martini | DWG NO. 005-301 | REV

SCALE 1:1 | DATE CREATED 2/21/2023 | DATE MODIFIED | SHEET 1 OF 1

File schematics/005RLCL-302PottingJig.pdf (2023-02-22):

.63

.28

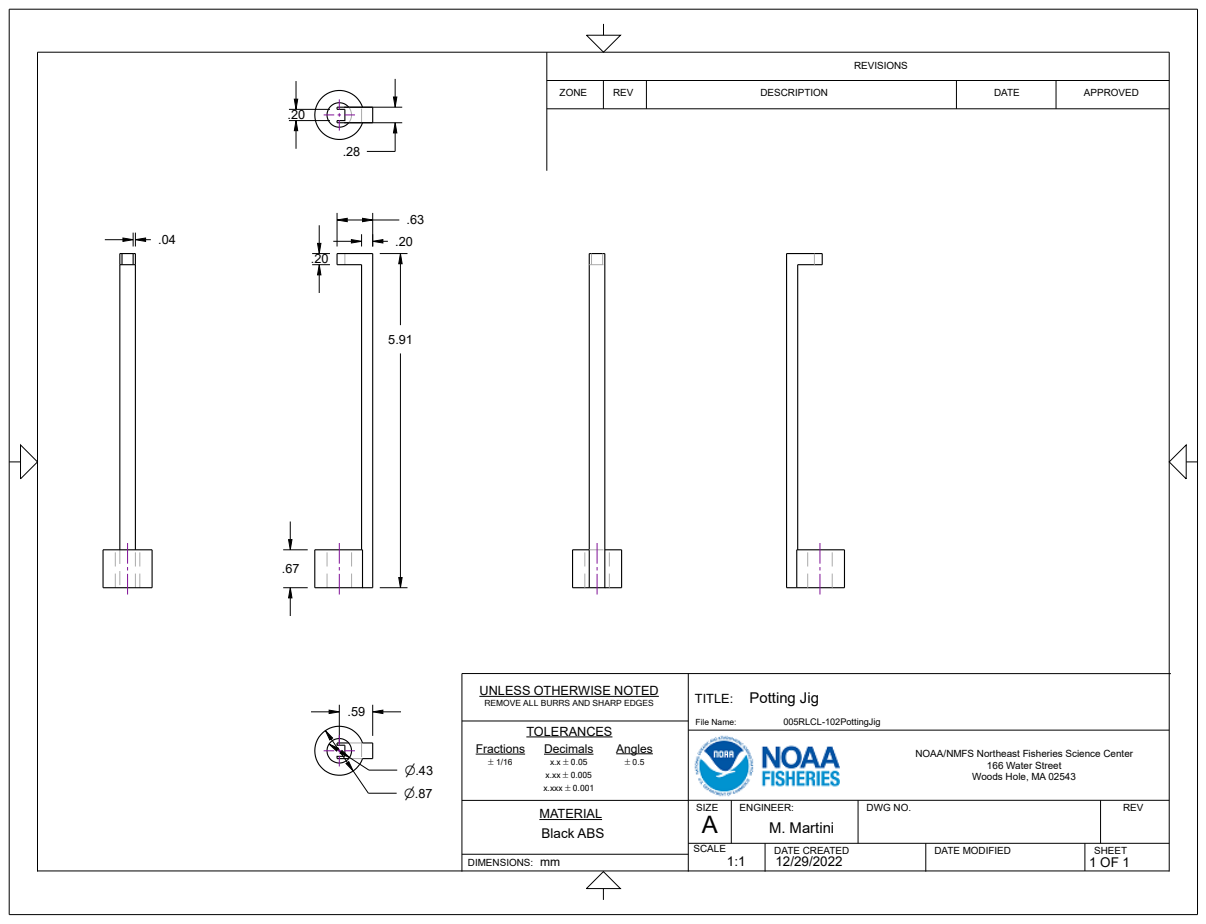
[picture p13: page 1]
DIMENSIONS:; Fractions `1/16; Angles `0.5; TITLE:; File Name:; Potting Jig; 005RLCL-102PottingJig

REVISIONS

ZONE | REV | DESCRIPTION | DATE | APPROVED

UNLESS OTHERWISE NOTED
REMOVE ALL BURRS AND SHARP EDGES
TOLERANCES
Decimals
x.xxx `0.001

NOAA/NMFS Northeast Fisheries Science Center

166 Water Street
Woods Hole, MA 02543

MATERIAL Black ABS | SIZE A | ENGINEER: M. Martini | DWG NO. | REV

SCALE 1:1 | DATE CREATED 12/29/2022 | DATE MODIFIED | SHEET 1 OF 1

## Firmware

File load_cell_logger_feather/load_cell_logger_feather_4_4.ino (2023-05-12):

/*
Firmware for underwater load cell logger - specific to the NEFSC version.

Original Author: Bill DeVoe, Marine Resource Scientist III, Maine Department of Marine Resources
Contact: william.devoe@maine.gov // bdevoe@gmail.com
Original Creation Date: 12/18/2019

License:  "THE BEER-WARE LICENSE" (Revision 42):
Bill DeVoe wrote this file.  As long as you retain this notice you
can do whatever you want with this stuff. If we meet some day, and you think
this stuff is worth it, you can buy me a beer in return.

Version History:
1.0: 5/21/2020 - Stable
2.0: 5/27/2020 - Bluefruit BLE supported
3.0: 7/17/2020 - Ported to Adafruit Feather M0 Express
3.1: 10/21/2020 - Simplified for production, no bluetooth
3.2: 11/19/2020 - Added option for monitoring LED, indicates logger recording, 
                  low battery, and if trip value has been reached.
  Fixed bug where calibration values were not being written to config file.
4.0: 12/27/2022 - Updated by M. Martini for NEFSC version of the load cell logger.  
                  Changed GPIO pins for LED control, using a common anode RGB LED
                  thus, pull down turns on the LED, so LED set values are inverted
4.1: 2/6/2023 - Updated, M. Martini to include real language for colors, and to make 
                  colors easier to change, as well as show version number in header.
4.2: 3/8/2023 - Updated, M. Martini, to return the weight entered, as the value might
                not always be correctly received depending on what serial terminal
                is used.  Increase the number of values averaged for a calibration reading.
4.3: 3/30/2023 - Updated M. Martini provide means to get gain information to user in a meaningful way

Description:
Logs values from a SparkFun Qwiic Scale NAU7802 to a SD card and specified intervals. 
Also allows for calibration of the load cell over a serial interface. Intended for 
use on a Adafruit Feather M0 Express with an Adalogger shield, but should work on other
Arduino boards with similar SD/RTC as Adalogger.

*/

#include "SD.h" // SD card
#include <Wire.h> // I2C
#include "RTClib.h" // Real time clock
#include "SparkFun_Qwiic_Scale_NAU7802_Arduino_Library.h" // Click here to get the library: http://librarymanager/All#SparkFun_NAU7802

// ***********************************************************************
// * MACROS
// ***********************************************************************
#define VERSION_MAJOR 4
#define VERSION_MINOR 2

// Wait for serial input in setup()?? 0 or 1
#define WAIT_TO_START    0

// Baud rate for serial port (over USB cable)
#define BAUD_RATE 9600

// ----- Default settings if not present in config file -----
// Default for echo to serial
#define DEFAULT_ECHO 1 
// Interval in milliseconds between samples
// was 250
#define DEFAULT_LOG_INTERVAL 1000 
// How many milliseconds before writing the logged data permanently to disk
// set it to the LOG_INTERVAL to write each time.
// Set it to 10*LOG_INTERVAL to write all data every 10 datareads, you could lose up to              
// the last 10 reads if power is lost but it uses less power and is much faster!
#define DEFAULT_SYNC_INTERVAL 10000
// Default load cell calibrations
#define DEFAULT_CAL_FACTOR 0
#define DEFAULT_ZERO_OFFSET 1000L
// Default trip value in LBF
#define DEFAULT_TRIP_VALUE 1700

// Size of serial input
#define SERIAL_SIZE 15

// Number of weights to average when calibrating
// was 4
#define AVG_SIZE 20

// The digital pin to light when an error occurs. Pin 17 is built-in RX LED, usually used when receiving serial data.
// The built in LED on pin 13 cannot be used since pin 13 is being used for the clock signal for the SD card.
#define ERROR_LED 17 

// Pins for an external RGB LED for monitoring load cell status
#define STATUS_RED 11
#define STATUS_GREEN 6
#define STATUS_BLUE 5

// Analog input to measure the battery voltage. On the Feather M0 Express pin A7 (GPIO #9) is connected to a voltage divider
// such that the LiPo voltage can be measured. But GPIO #9 has already been set to be GREEN on the RGB LED. (#10, the only
// remaining PWM pin, cannot be used as it is the Card Select pin for the Adalogger). Thus it becomes necessary to save the RGB
// state prior to reading the analog voltage on this pin, and then toggle the pin state back to output after checking the voltage.
// TODO - the previous version set things this way and in the battery drain test, battery was declared low (blue LED) 
//        half way into its useful life.
#define VBATPIN A7

// Low battery voltage
#define LOW_BATTERY_VOLTAGE 3.5


// ***********************************************************************
// * GLOBALS
// ***********************************************************************
// TODO: these should probably be rolled into a singleton class/OOP structure

// due to the common anode LED used for the NEFSC logger, pull down lights the LED
// so the colors are obtained as follows
// blue 255, 255, 0
int blue[] = {255,255,0};
// green 255, 0, 255
int green[] = {255,0,255};
// red 0, 255, 255
int red[] = {0,255,255};
// magenta 0, 255, 0
int magenta[] = {0,255,0};
// yellow 10, 10, 255
int yellow[] = {10,10,255};
// orange 0, 108, 255
int orange[] = {0,108,255};
// all off 255,255,255
int all_off[] = {255,255,255};

// the gain values for the gain settings NAU7802_GAIN_xxx
// note that 0b000=0 maps to a gain of 1 and 0b111=7 maps to a gain of 128 
// defined here so they can be displayed in a meaningful way later
int gain_value_table[] = {1,2,4,8,16,32,64,128};

bool settingsDetected = false; // Used to prompt user to calibrate their scale
bool fm; // File manager is active/inactive
char input;
char serial_data[SERIAL_SIZE];

// Create an array to take average of weights. This helps smooth out jitter.
float avgWeights[AVG_SIZE];
byte avgWeightSpot = 0;

// Variables for raw and calibrated load, max load encountered. 
// Max load thus resets each power cycle
long raw_load; 
float load;
float max_load = 0;

float cal_factor; // Value used to convert the load cell reading to lbs or kg
float zero_offset; // Zero value that is found when scale is tared
 
// Pin for the the SD card select line
const int chip_select = 10;

// Globals for settings. These are read/written to CONFIG file
bool echo;
int log_interval;
int sync_interval;
int trip_value;
int gain_setting = 0;

// Time the last log was saved
uint32_t log_time = 0;
// Time the card was last synced
uint32_t sync_time = 0; 

// Array of RGB state. Pin 9 is shared with the voltage divider so have to restore led state after battery check
int rgb_state[] = {255, 255, 255};  // common anode LED

// Create instance of the Real Time Clock class
RTC_PCF8523 rtc;
// Create instance of the NAU7802 class for the load cell
NAU7802 load_cell; 

// Global now
DateTime now;

// If using the web IDE and errors are generated "does not name type" after instantiating these classes - this means the web IDE is referencing the wrong library. 
// Load the library manually as per: https://forum.arduino.cc/index.php?topic=586330.0

// Output log filename and object
char filename[12];
File logfile;

// Battery tracking variables
float measuredvbat;

// ***********************************************************************
// * SETUP
// ***********************************************************************
void setup(void) {
  Serial.begin(BAUD_RATE);  
  Serial.println();
  
  #if WAIT_TO_START
    Serial.println(F("Type any character to start"));
    while (!Serial.available()) {
      Serial.println(F("Still waiting..."));
      delay(1000);
    }
  #endif // WAIT_TO_START
  
  // Set pin mode of error led
  pinMode(ERROR_LED, OUTPUT);

  pinMode(STATUS_RED, OUTPUT);
  pinMode(STATUS_GREEN, OUTPUT);
  pinMode(STATUS_BLUE, OUTPUT);
  
  // Splash screen
  Serial.println(F("----------------------------------------"));
  Serial.println(F("      Lobster Endline Tension Meter"));
  Serial.println();
  Serial.println(F("Created by Bill DeVoe, MaineDMR"));
  Serial.println(F("For questions, email william.devoe@maine.gov"));
  Serial.println(F("Updated for NOAA NEFSC by M. Martini"));
  Serial.println(F("For questions, email marinna.martini@noaa.gov"));
  Serial.print(F("Version "));
  Serial.print(VERSION_MAJOR);
  Serial.print(F("."));
  Serial.println(VERSION_MINOR);
  Serial.println(F("----------------------------------------"));
  
  // Initialize the SD card
  Serial.println(F("Init SD card"));
  // Make sure that the default chip select pin is set to
  // output, even if you don't use it:
  pinMode(10, OUTPUT);
  
  // See if the card is present and can be initialized:
  if (!SD.begin(chip_select)) {
    error(F("Card"));
  }
  Serial.println(F("SD card OK"));
  Serial.println();
  
  // Set up RTC
  Wire.begin();  
  if (!rtc.begin()) {
    error(F("RTC"));
  }

  if (! rtc.initialized()) {
    Serial.println(F("Setting RTC"));
    // Following line sets the RTC to the date & time this sketch was compiled
    rtc.adjust(DateTime(F(__DATE__), F(__TIME__)));
  }
  Serial.println(F("RTC OK"));
  Serial.println();
  
  // Set up load cell
  if (load_cell.begin() == false) {
      error(F("LC"));
  }
  Serial.println(F("LC OK"));
  
  // Increase to max sample rate
  load_cell.setSampleRate(NAU7802_SPS_320); 
  // Turn down load cell gain since we are using a large capacity cell
  // Gains of 1, 2, 4, 8, 16, 32, 64, and 128 are available. This can be adjusted
  // depending on the capacity of the cell.
  // Bill DeVoe's original gain setting was 16
  // for bench testing with nearly no load (say, 3kg=6.61 lb), try very high gain
  //gain_setting = NAU7802_GAIN_128;  
  gain_setting = NAU7802_GAIN_16;  // for real world
  load_cell.setGain(gain_setting);
  // Re-cal analog front end when we change gain, sample rate, or channel 
  load_cell.calibrateAFE();

  // Load system settings from file
  readSystemSettings();
  
  // Retrieve load cell calibration settings
  getCalibration();
  
  if (settingsDetected == false) {
      Serial.println(F("LC !cal"));
  }
  
  // Create new file based on current date and increment - 19122000.csv, 19122001.csv, 19122100.csv, etc
  now = rtc.now();
  sprintf(filename, "%02d%02d%02d00.CSV", now.year() % 1000, now.month(), now.day());
  for (uint8_t i = 0; i < 100; i++) {
    filename[6] = i/10 + '0';
    filename[7] = i%10 + '0';
    if (! SD.exists(filename)) {
      // Only open a new file if it doesn't exist
      logfile = SD.open(filename, FILE_WRITE); 
      break;  // Leave the loop!
    } // End if SD exists
  } // End for loop
  
  if (!logfile) {
    error(F("logfile"));
  }
  
  Serial.print(F("Logging to: "));
  Serial.print(filename);
  Serial.print(F(" at "));
  Serial.print(log_interval);
  Serial.println(F("ms interval."));
  Serial.println();
  
  Serial.println();
  Serial.println(F("Type the following menu commands at any time:\n l - Change logging interval\n s - Change card sync interval\n e - Toggle echo to serial\n z - Get current real-time clock time\n d - Set real-time clock time\n c - Calibrate load cell with known weight\n m - Manually calibrate load cell with known values\n v - Retrieve load cell calibration values \n t - Tare the load cell\n f - Enter the file manager."));
  Serial.println(F("Type menu CMD any time."));
  Serial.println();
  
  // Write the file header 
  logfile.println("millis,time,raw_load,load");    
  if (echo) {
    Serial.println(F("millis,time,raw_load,load"));
  }
  if (!logfile) {
    error(F("log file"));
  }

  // Set RGB to green for setup OK
  setRGB(green, 3);

  // If you want to set the aref to something other than 5v
  //analogReference(EXTERNAL);
  
} // End setup
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

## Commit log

2023-02-22 first upload of schematics, stl files, etc.
    [005RLCL-101HousingInternalMount.V4.stl, 005RLCL-102PottingJig.stl, 005RLCL-105HousingInternalMountLCend.V1.stl]
2023-05-12 Update for revisions to use a larger battery, larger housing, and some software refinements.
    [005RLCL-105HousingInternalMountLCend.V1.stl, 005RLCL-105HousingInternalMountLCend.V2.stl, 005RLCL-110HousingInternalMountLargeBatt.V2.stl]
2023-05-12 update for latest uploads, large housing, battery, etc.
2023-05-12 update for latest uploads, large housing, battery, etc. adding the pics
2023-05-12 Revert "update for latest uploads, large housing, battery, etc."
    This reverts commit cbefff2694c5e5fef1996f6c0d1a0507bbdfce40.
